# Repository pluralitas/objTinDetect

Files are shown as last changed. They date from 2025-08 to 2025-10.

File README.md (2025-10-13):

# Detection for objective tinnitus
This is a device used to detect objective tinnitus in the ear canal using a inear microphone.
## Hardwares
- Core: [Raspberry Pi 5](https://www.raspberrypi.com/products/raspberry-pi-5/)
- Touch Screen: [Raspberry Pi Official 7" LCD Touch Display 2 (SC1635)](https://www.raspberrypi.com/products/touch-display-2/)
- Sound Card: [Pi Sound](https://blokas.io/pisound/)
- Microphone: [RØDE smartLav+](https://rode.com/en/products/smartlav-plus)
- Adapters: [SC3, 3.5mm TRRS to TRS Adaptor](https://rode.com/en/products/sc3); [AV Adapter, 3.5mm to 1/4](https://www.googleadservices.com/pagead/aclk?sa=L&ai=DChsSEwiAj4-F19KOAxWxpGYCHeLsKiQYACICCAEQGhoCc20&co=1&ase=2&gclid=Cj0KCQjwkILEBhDeARIsAL--pjwNm1FiJPDzKa9fMI-j_-p9ddxbYZ-5g3uSl7_SHG9M49bfU8sTmjEaAmcCEALw_wcB&ohost=www.google.comcid=CAESVeD2XnBelKPjYt5ecPFCVxeILIl3LmNixfIlJWfDKJTCmltC4eD1GcUrxFUE8_TawnRX1jr0jJsh3dbwZ156sKJR0OTPHmSeGGqYniwUDoaGZ18CNiA&category=acrcp_v1_45&sig=AOD64_0r7GQa_UCVvws-wRXK3miZs0S86A&ctype=5&q=&nis=4&ved=2ahUKEwjpiYWF19KOAxX6SGwGHRVZG5YQ9aACKAB6BAgJEBo&adurl=)
- Heat sinks: [Raspberry Pi 5 Heatsink](https://www.raspberrypi.com/products/active-cooler/)
- Charger: [Raspberry Pi 5 charger](https://www.raspberrypi.com/products/27w-power-supply/)

### Extra Parts (Optional)
- 30mm M2.5 Standoffs
- 10mm M2.5 Standoffs
- 2x40 Stackable female pin header

## Setup
Front Screen display
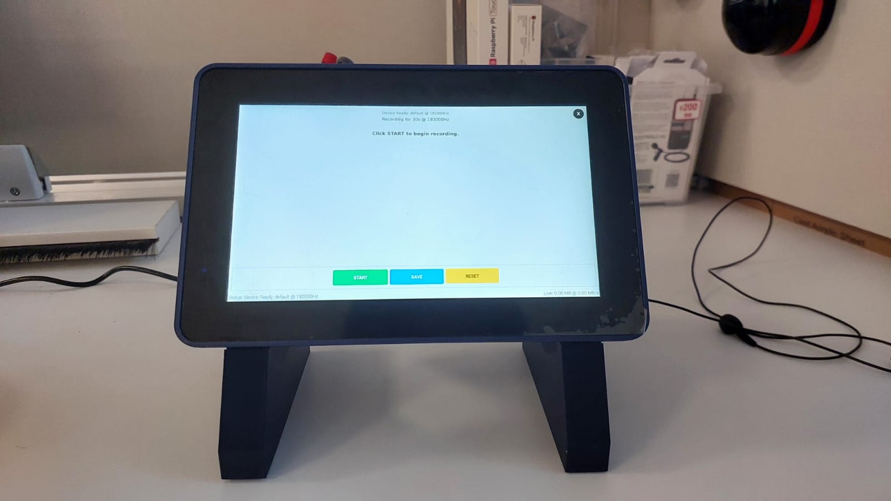
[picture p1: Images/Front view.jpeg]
Front View


Back View
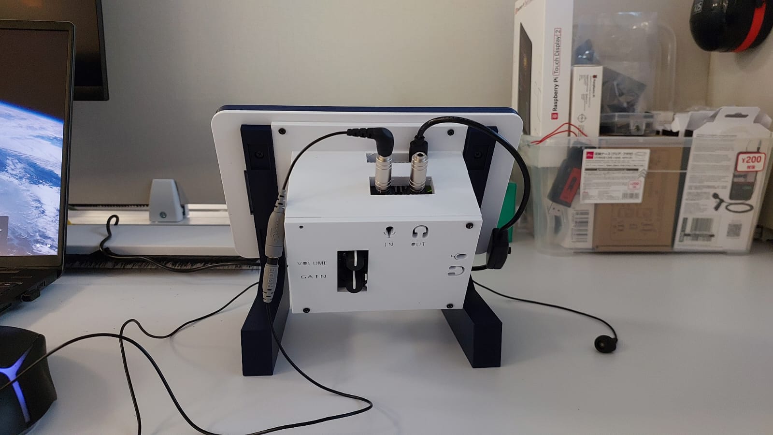
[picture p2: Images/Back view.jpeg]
Back View


Top View
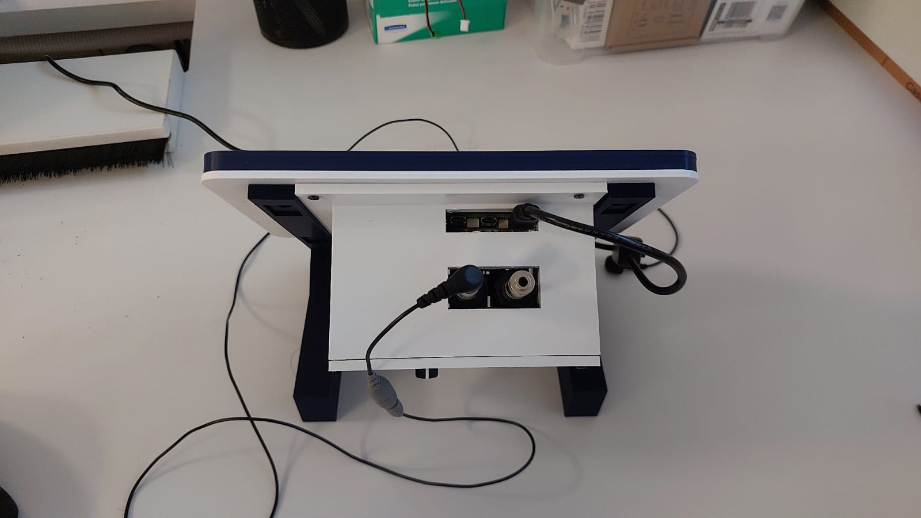
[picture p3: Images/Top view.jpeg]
Top View


Left View
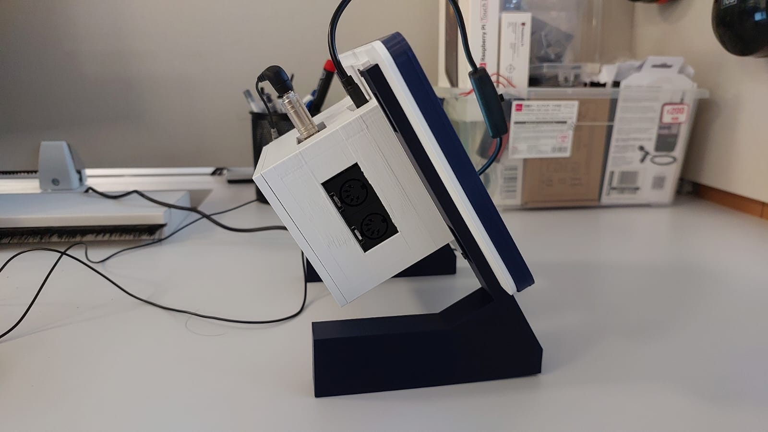
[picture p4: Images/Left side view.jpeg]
Left View


Right View
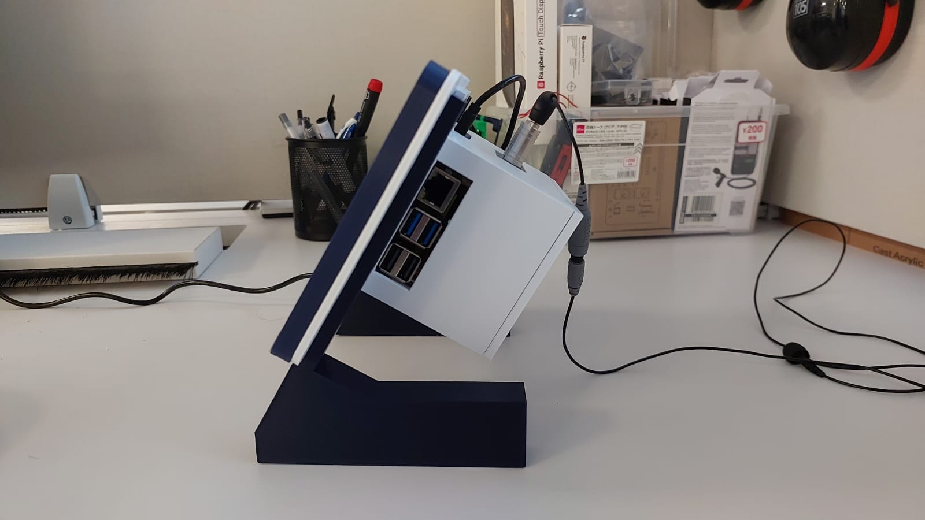
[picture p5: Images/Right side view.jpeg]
Right View


### Notes on the hardware setup
1. I had used 3 30mm + 10mm M2.5 standoffs to elvate the Pi Sound so that the DSI cable is not squished im between the heat sink and Pi Sound. The 2x40 stackable pin header was used to extend the pin's length so that the Raspberry Pi 5 GPIO pins can reach the Pi Sound.

2. I had used a SC3 3.5mm to convert the microphone's output from TRRS to TRS, afterwards it is then converted from 3.5mm to 1/4 stero using an AV adapter to connect to the PiSound.

## Objective Tinnitus Recorder python file (`audio_with_spectrogram.py`)

This application is a PyQt5-based graphical user interface (GUI) for recording audio, visualizing it as a waveform and a Mel spectrogram, and performing real-time analysis to detect and classify sounds as pulsatile or non-pulsatile. It is designed to find a compatible audio device automatically, record for a fixed duration, and then present the analysis results.

### Requirements

To run this application, you will need to have Python 3.9.21 installed, along with the following libraries:

- **PyQt5:** For the graphical user interface.
- **PyAudio:** To capture audio from the microphone.
- **NumPy:** For numerical operations on audio data.
- **SciPy:** Used for signal processing, specifically for finding peaks.
- **librosa:** For advanced audio analysis and Mel spectrogram generation.
- **wave:** For saving/opening the recorded audio to/from a `.wav` file.
- **Matplotlib:** For plotting the waveform and spectrogram.

### Configurations

You can customize the application's behavior by modifying the constants defined at the top of the audio_with_spectogram.py file.
***
#### Audio Recording Settings
These settings control the input device's configuration and the recording process.

- **TARGET_SAMPLE_RATE**: The sample rate in Hz for recording. The application will search for a device that supports this rate.

- **TARGET_CHANNELS**: The number of audio channels.

- **TARGET_FORMAT**: The data format for the audio stream. pyaudio.paInt16 represents 16-bit audio.

- **CHUNK_SIZE**: The number of audio frames per buffer. A smaller size may reduce latency but increase CPU usage.

- **DEFAULT_OUTPUT_DIR**: The name of the folder where recordings will be saved by default.

- **FIXED_RECORDING_DURATION_SECONDS**: The duration of each recording in seconds.

***
#### Spectrogram Parameters
These settings control the appearance and detail of the Log-Mel spectrogram.

- **SPEC_N_FFT**: The length of the Fast Fourier Transform (FFT) window. A larger value increases frequency resolution but decreases time resolution.

- **SPEC_HOP_LENGTH**: The number of audio samples between adjacent FFT windows. A smaller value increases the overlap and the time resolution of the spectrogram.

- **SPEC_N_MELS**: The number of Mel bands to generate, which determines the vertical resolution of the spectrogram.

- **SPEC_WINDOW**: The window function to apply before the FFT. Options include 'hamming', 'hann', 'blackman', etc.

***
#### Sound Detection and Analysis Parameters
These values tune the algorithm that classifies the audio.

- **WINDOW_DURATION_MS**: The duration (in milliseconds) of each chunk used to calculate the RMS of the signal. This affects the time resolution of the peak detection.

- **RELATIVE_THRESHOLD**: A ratio (std_dev / mean_rms) used to determine if a significant sound is present. A higher value makes the detection less sensitive.

- **DISTANCE**: The minimum required distance (in number of RMS samples) between detected peaks. This helps prevent detecting multiple peaks for a single sound event.

- **PULSATILE_BPM_MIN**: The minimum beats-per-minute (BPM) to be classified as "Pulsatile".

- **PULSATILE_BPM_MAX**: The maximum beats-per-minute (BPM) to be classified as "Pulsatile".

***
### Class description

#### `AudioController`

The AudioController class serves as the backend for all low-level audio operations. It abstracts the complexities of interacting with the pyaudio library and handles audio device management and data processing.

- Device Management
    - Initialize pyaudio instance.
    - Searches the system for a compatible audio input device that matches the configuration needed.
    - Returns a True if the suitable input device is found.
    - Stores the parameters of the input device.

- Audio Processing
    - Saves raw recorded audio frames into a `.wav`  file.
    - Opens raw recorded `.wav` files into audio frames for analysis.
    - Converts raw byte frames into a Numpy array (`y`).
    - Generates the Log-Mel Spectrogram (`S_mel_db`).

- Stopping
    - Uses a `close()` to terminate pyaudio when closing application.
***
#### `AudioWorker`

This class is a QThread designed to perform the audio recording in the background. By offloading the recording task to a separate thread, it ensures the main application window remains responsive and does not freeze during the recording process.

- Background Recording
    - The `run` method creates a new pyaudio stream to continuously read audio data in chunks `CHUNK_SIZE` until the recording is stop automatically (`FIXED_RECORDING_DURATION_SECONDS`) or manually (Stop Button).

- UI Update
    - Uses `pyqtSignal` to update on the `MainWindow`.
    - `progress_updated`: Emits the elapsed and remaining time to update the progress bar.
    - `status_updated`: Emits status messages to be displayed in the UI.
    - `recording_finished`: Emits the list of recorded audio frames back to the main window upon successful completion.
    - `recording_error`: Emits an error message if an exception occurs during the recording process.

- Stopping
    - Uses a `stop()` to allos the main thread to interrupt the recording loop early when the user uses the Stop Button.
***

#### `AudioPlayer`
This class is a QThread designed to play the audio recordings. When playing the audio, only the "Play/Stop" button is active.
***
#### `ClickableLabel`
A simple class that extends `Qlabel` to add a click functionality.
***
#### `SoundAnalyser`
This class is the core algorithm for analyzing the recorded audio to determine if it contains sounds and then classify it into pulsatile or non-pulsatile.

- Audio Analysis
    - Takes in the raw audio waveform (`y`) and sample rate (`sr`)
    - Normalises the audio signal to [-1,1]

- Sound Detection
    - Computes the rms of the graph to get the power of the signal
    - Determines if a significant signals is present by comparing the standard deviation of the RMS values to their mean (`relative_ratio` > `RELATIVE_THRESHOLD`).
    - Returns a true value if there is sound detected or else a false value and "No Sound" text to be displayed

- Pulsatile Classification
    - If sound is detected, it crops the waveform to remove the noise floor. Afterwards it performs peak detection on the cropped rms waveform(`cropped_rms`) to find the distinct peaks.
    - Calculates the intervals between these peaks to determine an average Beats per Minute (BPM)
    - Classfies the sound as "Pulsatile" or "Non-Pulsatile" based on whether the calculated BPM falls within the `PULSATILE_BPM_MIN` and `PULSATILE_BPM_MAX thresholds`.
***
#### `MainWindow`
The MainWindow class controls the UI of the application. It inherits from QMainWindow and is responsible for creating the user interface, managing the application's state, and coordinating the interactions between the user and the backend classes (`AudioController`, `AudioWorker`, `SoundAnalyzer`).

- UI Management
    - Builds and Organise all the UI elements (Button, labels, progress bar and layouts)
    - Uses `QstackedWidget` to manange the 3 primary application pages (idle, Recording and Analysis)
    - Embeds Matplotlib `FigureCanvas` widgets to display the waveform and spectrogram plots

- State and Logic Controls
    - Initialise and hold instances of `Audiocontroller` and `SoundAnalyser` 
    - Manages the application's flow: Checking device status --> start recording --> handling record completion --> resetting for a new recording or closing the application.

- Event Handlling
    - `handle_start_stop()`: Starts or stops the `AudioWorker` thread.
    - `handle_save_as()`: Opens a file dialog and saves the recorded audio by calling `audio_controller.save_audio_to_file()`.
    - `handle_finish_reset()`: Resets the UI and application state back to idle.
    - `handle_recording_completion()`: A slot that receives the recorded data from `AudioWorker`, triggers the analysis and plotting, and updates the UI to the analysis page.

- UI Updates
    - Connects to signals from the AudioWorker to update the progress bar and status messages in real-time.
    - Calls `update_analysis_plots()` to render the waveform and spectrogram visualizations after a recording is complete.
    - Manages the visibility and content of the result label ("Pulsatile", "Non-Pulsatile", "No Sound", "Error").

- Closing event
    - Handles the application's `closeEvent` to ensure the `AudioWorker` thread is stopped and the `AudioController`'s resources are released properly upon exit.
***
## Verification of the heart sound audio
### ECG and Audio Recording Comparison (`ECG_vs_Audio_Recording_Test.ipynb`)
`ECG_vs_Audio_Recording_Test.ipynb` provides a Python script designed to analyze and compare Electrocardiogram (ECG) signals with corresponding heart sound audio recordings base on their BPM.
***

### Results Summary
The numerical outputs from this script (such as mean BPM, t-statistic, and p-values) are printed to the console during execution.

A comprehensive summary of the key findings and final results for all processed recordings has been compiled and is available in the accompanying Excel file:
[`Comparison analysis of ECG and Audio waveforms.xlsx`]
*** 

## Classification ALgorithm test
`Audio_Classification_Test.ipynb` provides a Python script designed to analyze audio recordings (.wav files) to perform two key tasks:
1. Sound vs. Noise Classification: It classifies an audio segment as either a meaningful "Sound" (e.g., pulsatile tinnitus) or ambient "Noise" based on the signal's amplitude variance.
2. BPM Detection: For signals classified as "Sound," it identifies rhythmic peaks and calculates the corresponding Beats Per Minute (BPM).
***

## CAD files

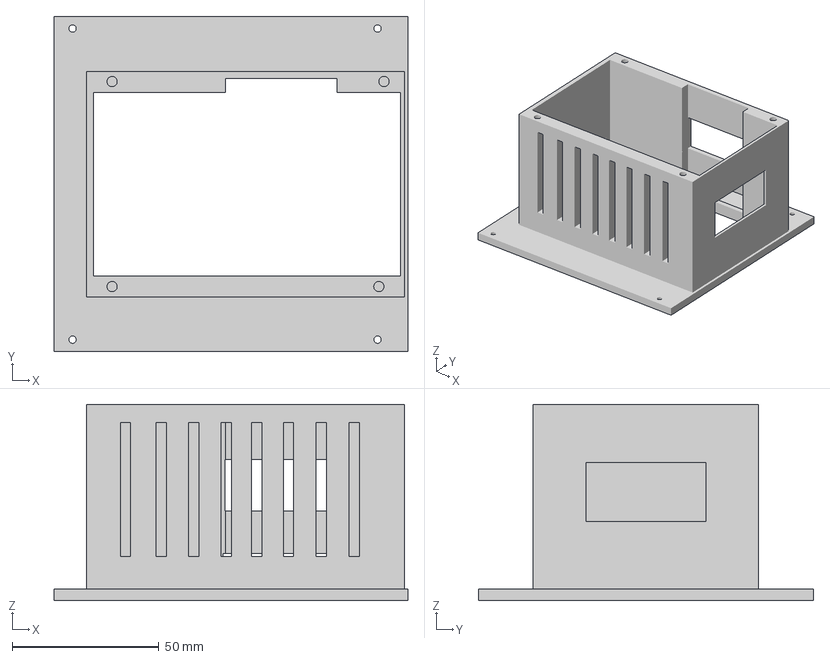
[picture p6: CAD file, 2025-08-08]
3D print/Box (4).step
120.6 x 114.3 x 66.8 mm

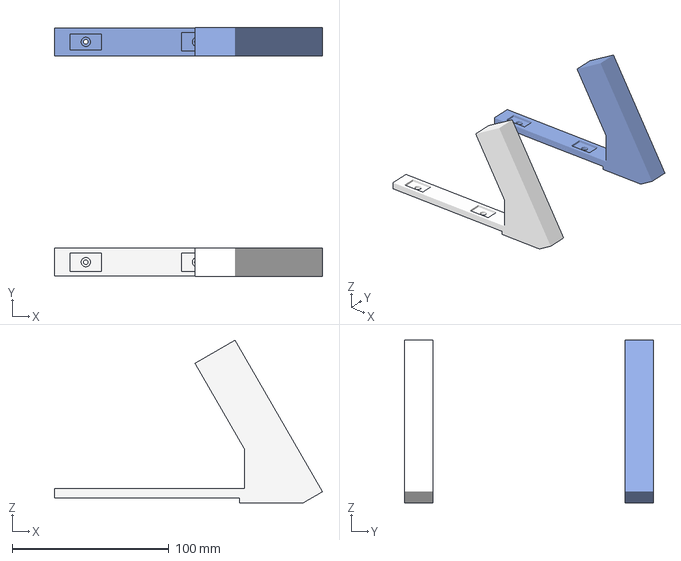
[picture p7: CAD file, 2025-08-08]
3D print/Stand (1).step
171.2 x 158.8 x 103.9 mm

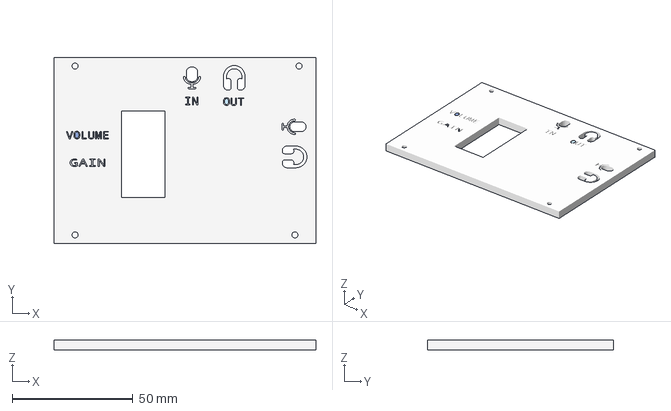
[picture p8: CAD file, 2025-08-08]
3D print/Box cover (2).step
108.4 x 76.8 x 3.97 mm

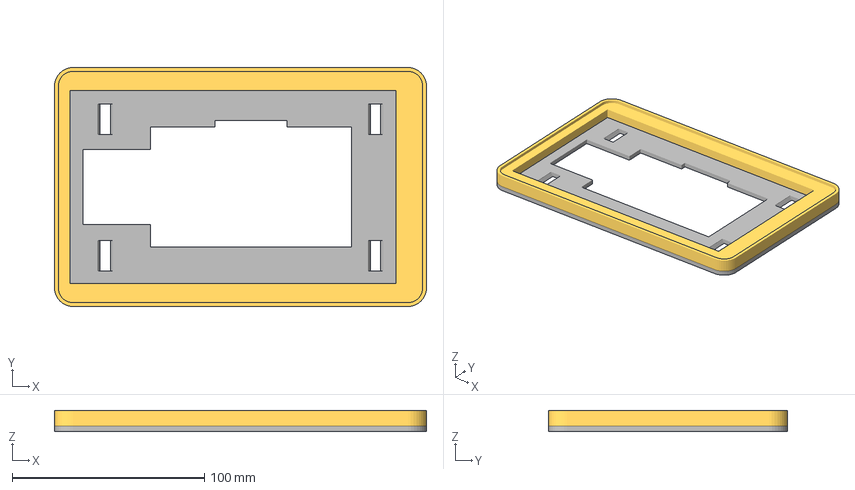
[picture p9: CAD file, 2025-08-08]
3D print/base plate (1).step
193.8 x 124.5 x 11.0 mm

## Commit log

2025-07-30 readme update
    Update readme with ecg comparison
    [Comparison analysis of ECG and Audio waveforms.xlsx, Sub_A_PushUps.csv, Sub_A_Rest.csv, Sub_B_PushUps.csv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]
2025-08-05 3D prints
    Added in 3D prints for the casing of the device
    [Stand.step, base plate.step]
2025-08-08 Images
    Updated new images of the new device
2025-08-08 3D print
    Added in new 3D print files
    [Box (4).step, Box cover (2).step, Stand (1).step, Stand.step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]
2025-09-17 update audio_with_spectrogram.py
    *changed sampling bit rate from 16bit to 24bit
    *converted buffer medium "frames" from 2 bytes (np.int16) to 4 bytes (np.int32) to accommodate the 24bit samples.
    *CAUTION: may crash if run on systems with audio card that does not support 24bit sampling.
2025-10-14 Update audio_with_spectogram.py
    - Changed recording timing back to 30s
    - Update Audioplayer to join frames and play directly from bytes
